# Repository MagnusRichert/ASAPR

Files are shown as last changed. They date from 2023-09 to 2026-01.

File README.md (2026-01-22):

# ASAPR - Advanced Scratch Assay Plotting Robot

This repository contains the code to execute in vitro cell analysis via scratch assays as done in the paper ["Scratching in style: 3D printers as plotters for automated and complex wound-healing assays"](https://doi.org/10.1016/j.isci.2025.114230). We greatly appreciate any feedback, contributions, or other input and questions you may have!

## How to use this repository

Here we will discuss how to use this repository for your scratch assay and what you need.

### Bill of Materials

- 3D-Printer that supports M0 command (preferrably with autoleveling sensor)
- Frame to hold your well plate
- 7mm wrench
- Adapter from M6 thread to tip
- Spring loaded pipette tip

These are the general materials you will need. The specific components used in the preprint are detailed in the BOM.xlsx file.

### Preparation of Printer

This chapter covers all the essential steps to prepare the printer. If you don't have access to a second printer for printing the frame, it's recommended to use the printer intended for scratching to print it. Be aware that whenever you home the printer, the tip should be removed to avoid it being driven into the build plate, which could cause damage!

#### Replace the nozzle

The first step is to remove the nozzle of the old printer with a 7mm wrench. Afterwards screw in the adapter with M6 thread that will be used to hold the tips. As described in the preprint there are two different approaches used to mount the probe to the printer. The first approach was to use a drill chuck holding the spring-loaded test probe while being inserted into a 3D-printed mount, considering that most of the 3D-printers have a M6 thread to hold the nozzle this method was not very straightforward. So the second approach was to 3D print a M6 Adapter as a direct replacement to the nozzle. 

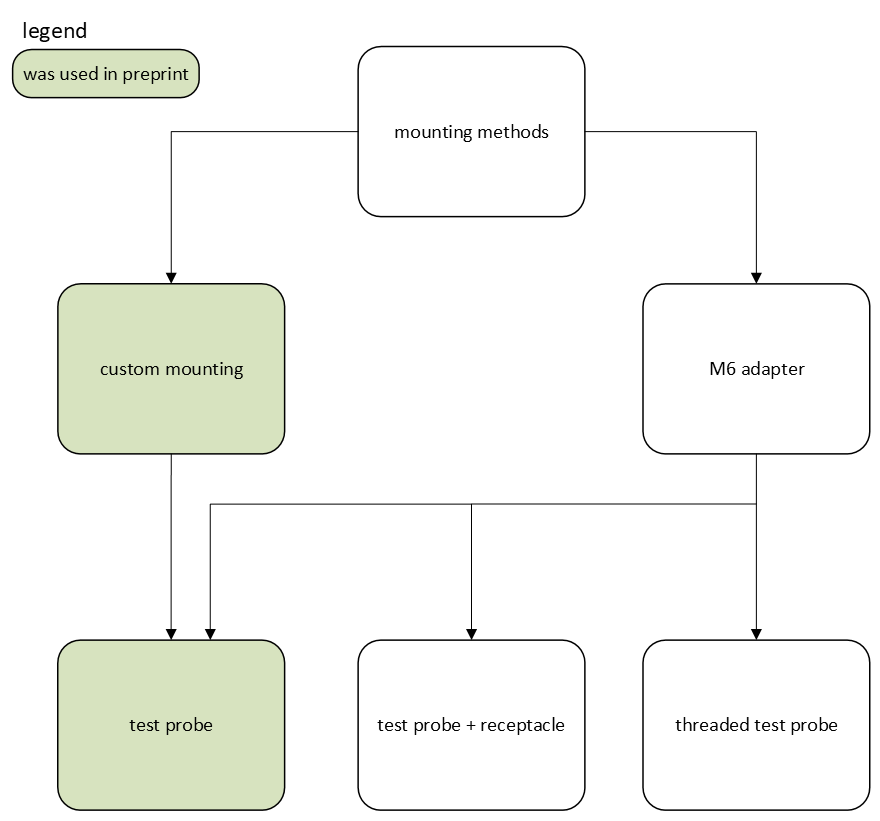
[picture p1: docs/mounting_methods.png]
mounting methods


As you can see there are multiple ways of mounting the test probe to the Printer, where three of these were used in the preprint. The other methods are still in work and not verified yet but may offer a few advantages.
When selecting the test probes for ASAPR there three main requirements to be fulfilled:

  1. The total length of the test probe must be greater than the depth of the well
     (in our case the length had to be at least 20mm excluding the part sitting in the Adapter)
  2. The width of the test probe must be wider than the inner diameter of the pipette tip
  3. The test probe should have a conical tip
     
You might also want to take a look at the force of the spring at the given compression point. We always looked for test probes with a spring force of 1.5N at the recommended working stroke provided in the datasheet. As the recommended working strokes are different for some test probes the spring force should be within the same order of magnitude. Furthermore you should take a look at the wobble of the test probe which describes the deflection of the tip from its ideal position due to the necessary play between the piston and the probe sleeve. To give you some idea of possible test probes, here are a few examples from the company INGUN Prüfmittelbau GmbH.

test probes:
- GKS-050 201 050 A 1500 
- GKS-912 201 060 R 1504 +KS-112 (currently supported)
- GKS-112 201 080 R 1504 +KS-112 (currently supported)
- GKS-112 201 100 A 1504 +KS-112 (currently supported)
- GKS-204 201 130 R 1510

threaded test probes:
- GKS-075 201 064 A 1502 M 
- GKS-112 201 080 R 1502 M (currently supported)
- GKS-112 201 100 R 1502 M (currently supported)
- GKS-204 201 130 R 1510 M
- GKS-503 201 180 R 1502 M (currently supported)

#### Level the printbed (Not needed with autoleveling)

To level the print bed, start by homing the printer, then disable the motors to allow free movement of the printhead in the XY-plane. Slide a sheet of paper between the adapter in the printhead and the print bed. Visit each corner and adjust the screws by tightening or loosening them until you feel slight resistance when moving the paper. Ensure the resistance is consistent across all corners. Alternatively, you can level the bed visually, making sure the distance between the adapter and the print bed is uniform at each corner. The exact distance isn't crucial, as the Z-offset will be set later.

#### Autolevel the printbed

If you want to use auto-leveling, you must first delete any old mesh, then create and save a new one for your print bed. The necessary actions can be found in the printer settings. For detailed guidance, there are many online tutorials available that explain this process step by step.

#### Mount the positioning for your wells

The next step is to mount your positioning guide for the well on the build plate. It's important to ensure the sides of the guide or well align with the X and Y axes. A magnetic print bed is not recommended, as it may slip and lose its position. If you're working with wells of different sizes, it's recommended to use permanent position guides in the lowest XY corner and variable guides for the other sides (see the picture below).

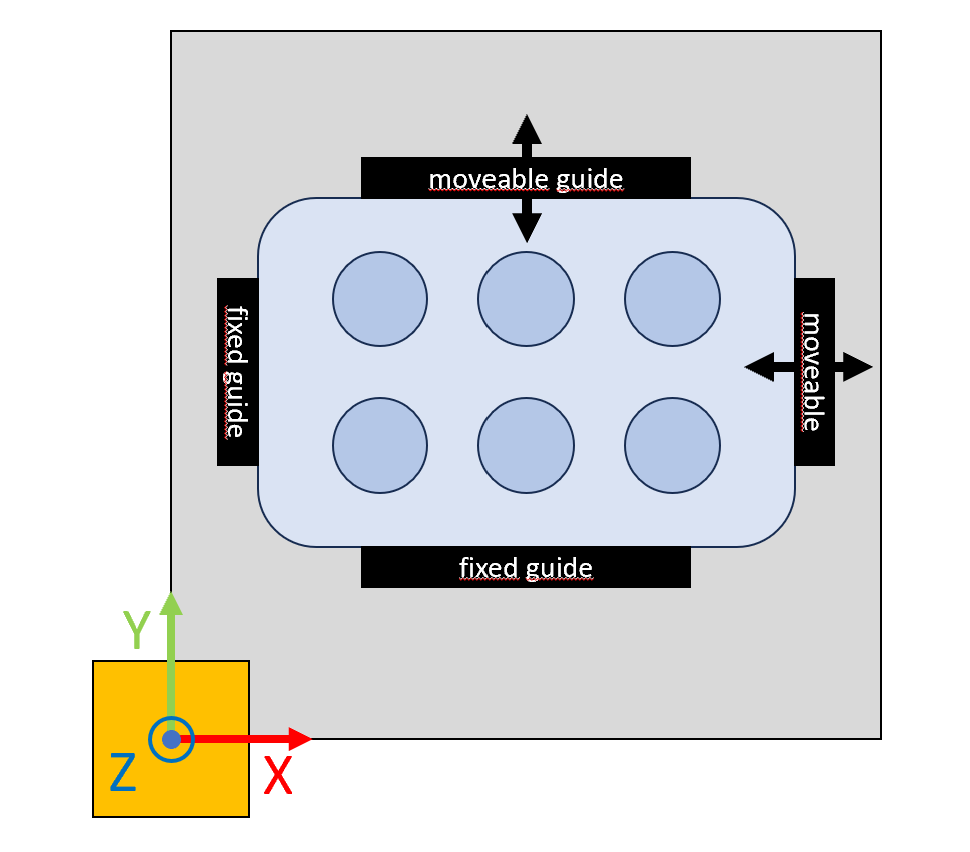
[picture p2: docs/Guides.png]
Guides


This setup allows you to determine the x_offset and y_offset only once. The offsets are shown in the picture below.

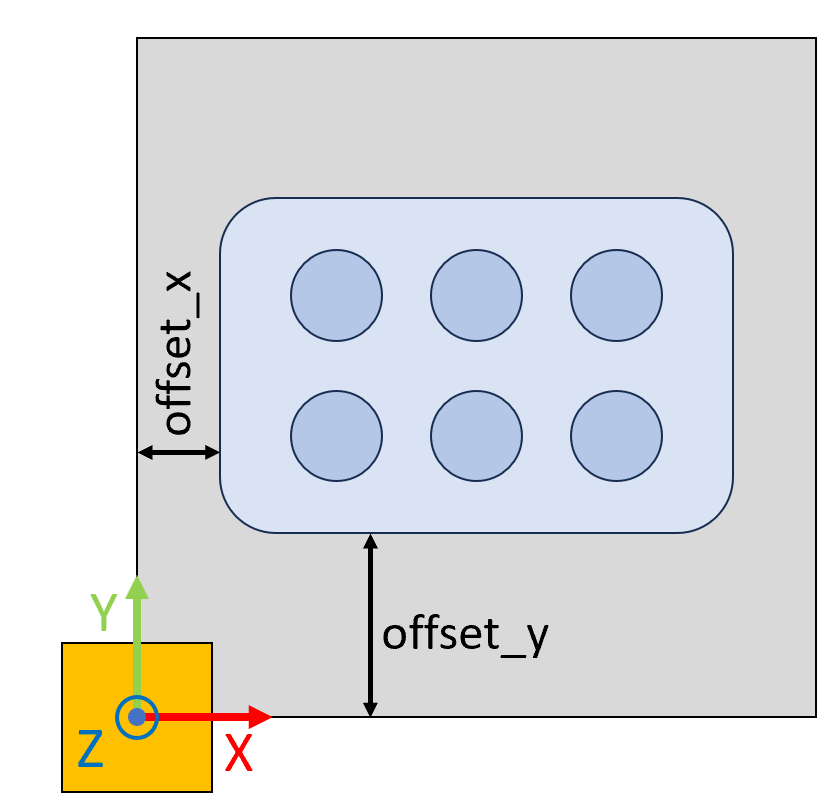
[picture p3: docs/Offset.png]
Offsets


The positioning guide used in the preprint can also be found in this repository. It can be printed using the same printer that will be used for scratching.

#### Measure offsets

There are two approaches to determining the offsets. The first method uses the printer's built-in "move" function and can be applied to any printer. The second method involves manually measuring the offset from the coordinate origin.

##### Using the printer

To measure the offsets, start by homing your printer and placing the well on the build plate. Use the printer's "move" function to raise the Z-axis high enough to insert a tip. As you move the axes, the printer will display the current position, which is the offset you need.

First, move the tip to the X and Y edges closest to the home position, ensuring it barely touches the edges. For instance, in the example image, the printhead was moved to 24.8mm for the Y-axis:
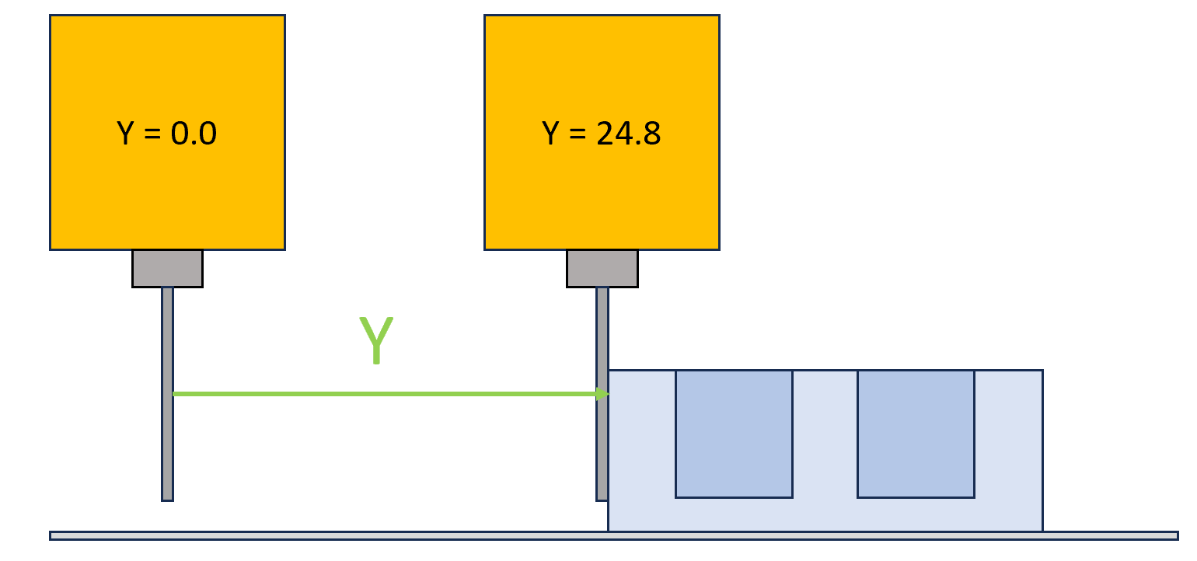
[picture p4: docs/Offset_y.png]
Offset Y

To calculate the offset for X and Y, add the radius of the tip used. For example, if the tip diameter is 0.4mm, the offset for Y would be: offset_y = Y + d/2 = 24.8mm + 0.2mm = 25.0mm

For the Z offset, move the printhead until the tip touches the well, as shown:
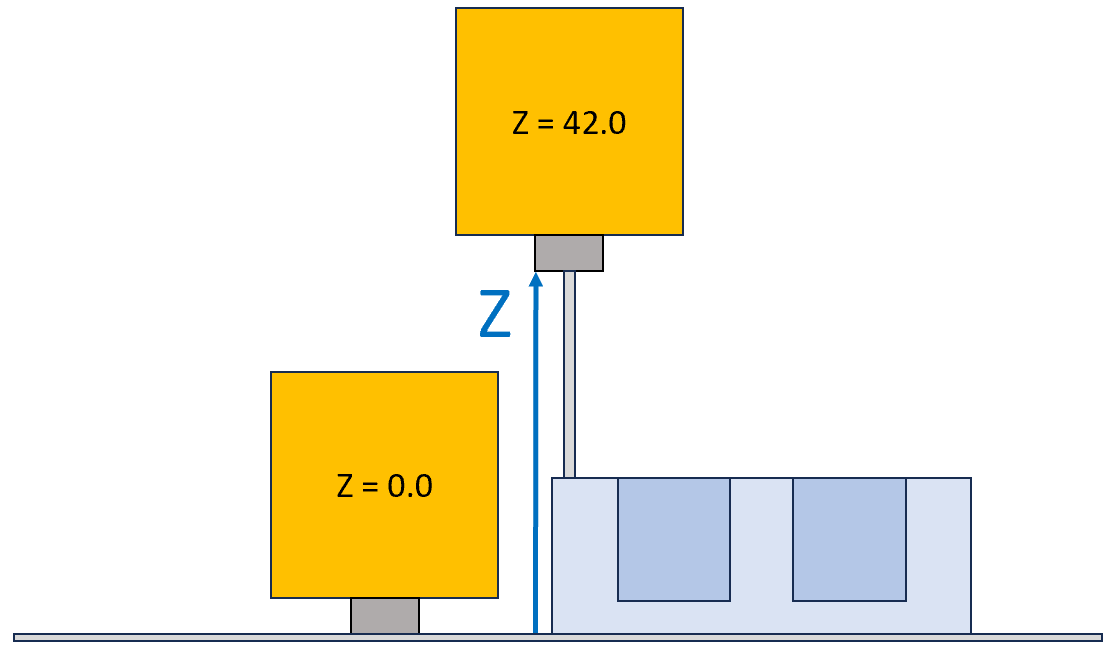
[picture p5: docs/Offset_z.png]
Offset Z

The Z value displayed can be used directly as the offset. If you change the tip, you'll need to adjust the Z offset by either remeasuring or calculating the difference in length between the tips and adjusting accordingly.

##### Calculating from coordinate system

This approach can be used if the printer's coordinate origin is marked on the build plate. You can simply measure the distance between the well plate and the origin in the X and Y dimensions using a caliper gauge. However, the Z offset still needs to be determined using the method described above, by moving the printer until the tip touches the well.

##### Fine tuning by test runs

The easiest way to set the X- and Y-axis offsets very accurately is to use an empty cell culture plate and scratch a cross through it using a test probe without a pipette tip attached so that the well surface is actually damaged. To do this, select the “mesh” option in the script with a 90° rotation and a generous tip offset to avoid hitting the edges of the plate in case of doubt. The test probe should not be driven too deeply into the plate in order to avoid tilting the tip and possible bending. You can then measure the localisation of the cross within the plate with a caliper and adjust the coordinates if necessary. Recommended is for example to measure all corners of a 24-well plate. Run again until it fits your needs.
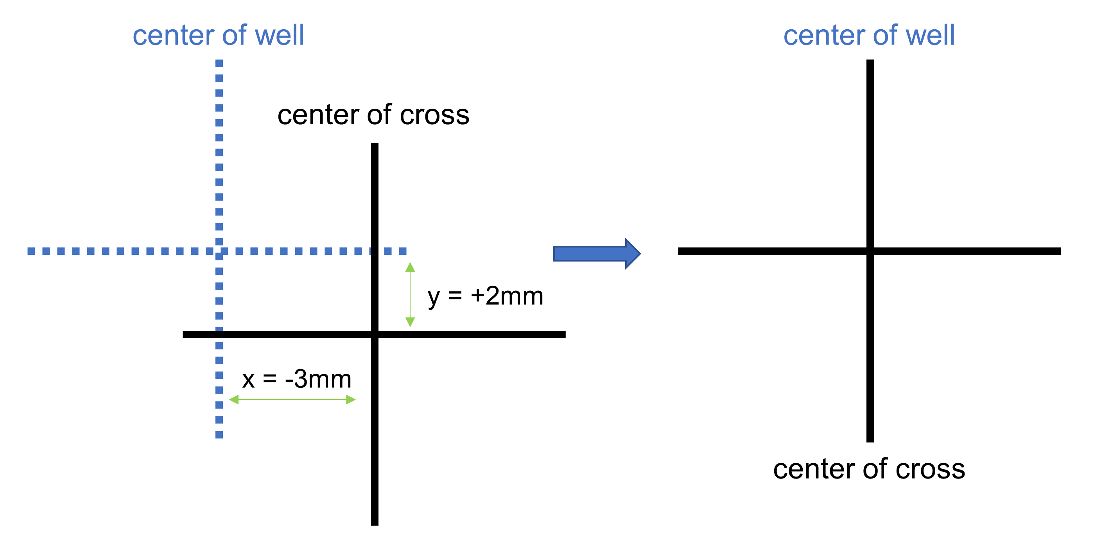
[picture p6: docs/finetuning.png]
Fine Tuning


#### Prepare well file

The program reads well dimensions from a file, which you will need to input manually based on your well. These specifications can typically be found in the product's technical documentation or you can measure them yourself. An example file for a four by six well plate is provided in the repository. It contains the following dimensions:

~~~bash
number_x: 3
number_y: 2
diameter: 15.5
depth: 17.3
distance_well: 3.5
distance_x: 7.8
distance_y: 6.0
~~~

The values for number_x and number_y represent the number of wells along the x and y axes, respectively. Be aware that they depent on the orientation of your well. The remaining dimensions are displayed in the image below.
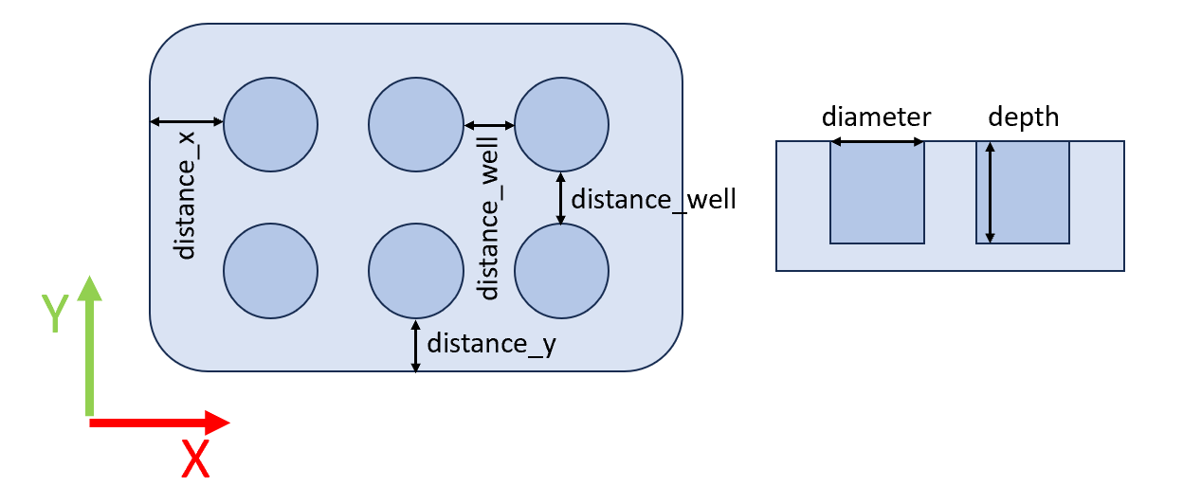
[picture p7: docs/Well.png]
Well Dimensions


### Preparation of your PC

You will need an installation of python version 3 or newer. When installing check the box that says "Add Python to PATH". Afterwards open a command window like powershell or cmd and enter the following commands sequentially:

~~~bash
python -m ensurepip --upgrade
pip install svgpathtools
~~~

This will install the python package manager and the package svgpathtools which is needed to process vector graphics.

### Script usage

After measuring all the required offsets and preparing your PC, you’re ready to use the script. If Python is installed correctly, you can simply double-click ASAPR.py to run it.

The GUI will appear as shown below:
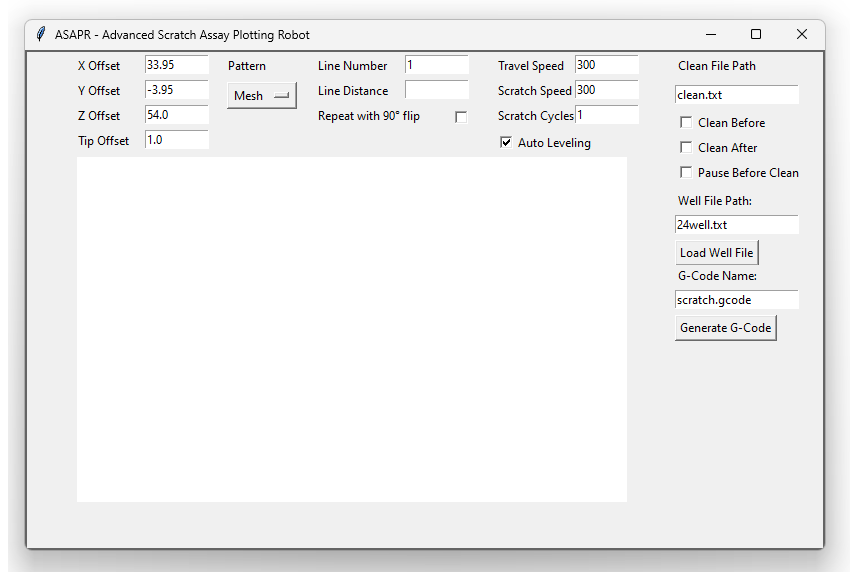
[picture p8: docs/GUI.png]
GUI


#### Enter offsets

In the top left of the GUI, you need to enter your measured offsets in millimeters. The tip offset specifies the minimum distance between the center of the tip and the well wall. This value MUST be at least half of the tip diameter. For more robust scratching, you might consider increasing this offset to 1-2 mm.

#### Choose pattern

Next to the offsets you can choose between between three different patterns: mesh (mutiple lines), circles and svg grapics.

##### Mesh

The mesh pattern is defined by the number of lines and the distance between them. You can also just choose to scratch a single line through the center of the well. If the "Repeat with 90° flip" box is checked, the mesh will be scratched again rotated by 90° to create a criss-cross pattern.

Mesh

##### Circles

The circles pattern is defined by the number of circles, the distance between them, and the diameter of the innermost circle.

Circles

##### SVG

To scratch a vector graphic, place the file in the same folder as ASAPR.py and enter its name. The SVG should contain only lines and curves, which can be filled. For this you can specify the overlapping area between the fill lines from 0 to 1 (0 to 100%). Currently only the fill property of the style attribute is supported, so not all SVG Files will work. Best practice is to generate a new basic SVG File with inkscape and not to use complex forms or properties. The scratch will follow the lines like a trajectory, so you can create larger surfaces by placing lines close to each other. The SVG will be scaled automatically to the maximum size that fits within the well. If you want it to be smaller, you can adjust the scale parameter to values between 1 (maximum size) and 0 (essentially a point).

SVG

#### Movement settings

Next to the patterns, you can set the movement speed of the printhead during both movement and scratching, in mm/s. Note that there are limitations to these speeds in the printer settings, especially for the Z-axis speed. If you want to scratch your pattern multiple times, you can increase the "Scratch Cycles" value from 1 to however many cycles you desire. To enable the auto-leveling function of your printer, check the corresponding tickbox.

#### Cleaning

To clean the tip before or after scratching a well plate, you can set up one or more cleaning containers and specify their coordinates in a "clean.txt" file. The cleaning process involves moving the tip in a specified number of circles within each container. Below is an example of the file content format:

~~~bash
X: 150
Y: 120
Z: 30
Radius: 4
Depth: 10
Number: 20
/
~~~

In this file, each section describes a cleaning container, with Number specifying the amount of circles, Depth indicating how deep the circles will be relative to the specified Z coordinate, and Radius defining the size of the circles. The "/" marks the end of the data for one container, and you can add as many sections as needed in one file.

When the "Pause Before Clean" checkbox is ticked, the tip will pause 1 cm above the specified XYZ coordinates. This allows you to position your cleaning container more easily without needing to measure the coordinates precisely.

##### Desinfecting
To disinfect the tip, it is sufficient to immerse it in 70% ethanol for at least 30 seconds and then allow it to air dry. It is also recommended to rinse the tip in ethanol after each scratching process to remove debris. During the test phase, several scratched wells plates were incubated for at least one week and contamination was never observed. It is also possible to prepare several tips and autoclave them in advance, but it is not necessary to replace them after each use.

#### Load well setting

On the right side of the GUI, you'll need to provide the well data. Since wells are often standardized, the data is read from a *.txt file for ease of sharing, modification, and reuse. An example file named "24well.txt" is included in the repository.

#### Select wells to scratch

After loading the well file, the layout will be plotted in the central area of the GUI. Clicking on a well will turn it red, indicating that it will be excluded from scratching. You can also click and drag your mouse to select or deselect multiple wells underneath. The well located in the bottom left corner represents the one closest to the coordinate origin, which is typically the home position of your printer and usually corresponds to the bottom left corner of the print bed.

#### Generate G-Code

The final step is to enter the name of your *.gcode file and to generate the G-Code. BEFORE running it on the 3D-Printer be sure to read the next chapter for important instructions. In the future there might be the option to send the generated G-Code right from the GUI over W-Lan, until then you need to save the G-Code on a SD-Card and plug into the 3d-printer.

##### Individual customisation of the G-Code

Some printers may require individual adjustments, especially in the header section of the Gcode. For example, the Prusa MK3S+ requires an additional 'W' after the G28 command to suppress auto levelling, which is not possible in the setup due to the fixed plate holder. These adjustments can easily be made in the text file of the finished Gcode. An option to customise the header of the Gcode for each printer individually is planned.

~~~bash
G28 W
~~~

### Running the G-Code

Before running the G-Code on your machine, ensure that the bed is leveled or properly prepared for the auto-leveling option. The guides and well should be correctly positioned by now. Additionally, remove the scratching tip, as the printer will home before starting the scratching process; leaving the tip in place could cause it to be driven into the print bed. If the printer does not home the Z axis above the print bed, but at the end stops of the upper area, the tip can always be left in place.

Once you start the print, the "M0" G-Code command will pause the printer before scratching, allowing you to insert the tip. Verify that your printer firmware supports this command. After inserting the tip, continue the print, usually by pressing the knob.

You can preview how your scratches will look by pasting your G-Code into a viewer. One option is ncviewer.com, though keep in mind that for larger X and Y coordinates, the depiction might be shifted. Despite this, the G-Code will still function correctly on your printer.

## Outlook

A lot of ideas went into this project and even more were discarded. There is certainly room for improvement in every nook and cranny, so we would be delighted to receive any valuable input for the further perfection of this project. Be it software improvements or better materials such as a Teflon tip, etc. Your input is always highly appreciated!

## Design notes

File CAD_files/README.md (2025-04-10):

# CAD files

In this section we want to go into detail on how to print and assemble the needed parts mentioned in the BOM file.

## frame

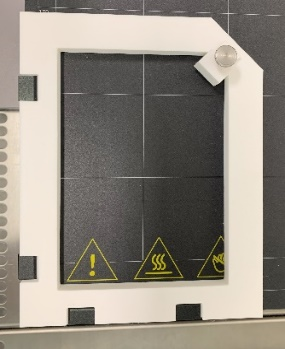
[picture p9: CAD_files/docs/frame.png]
frame


The frame is supposed to hold the well plate on the print bed while maintaining a fixed position consistently. The frame itself is attached with four clamps designed for glass print beds. For the frame you need in total four pieces, of which are two 3D-printed. Both of these parts are included in the file "frame".
In general there are two things which have to be considered when printing the frame. Since the frame features some floating areas you want to enable some kind of support, preferably tree support for printing. Moreover it is preferred to add some kind of modifier in the area of the slider to increase the infill density since this section of the frame is under more mechanical stress.

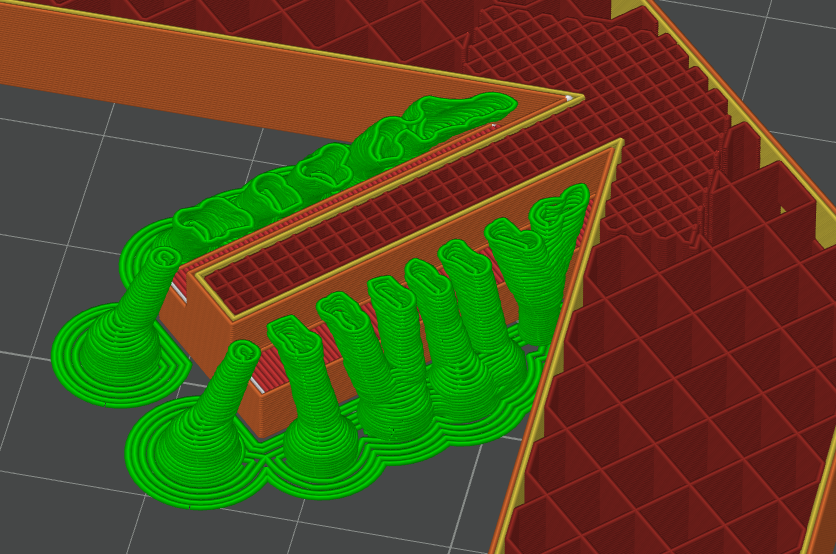
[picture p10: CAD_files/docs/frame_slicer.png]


As you can see tree support was used while achieving a higher infill density in the slider area. The frame itself was printed with an infill density of 15% while the area of the slider has an infill density of 70%. Every part was printed with a 0.4mm nozzle and a layer height of 0.2mm using white PLA on the BambuLab A1 mini.

Since the screw for securing the slider on the frame has to be screwed in and out a few times we decided to use an M3 threaded insert for the slider. This ensures a tight fit of the screw even after several iterations of use. Last but not least you need an M3 knurled knob for the slider.
These two parts are more or less optional since you could also think of just using a normal M3 screw without threaded insert.

print settings:
- infill density: 15%-70%
- nozzle diameter: 0.4mm
- layer height: 0.2mm
- material: PLA

## M6 adapter

The M6 adapter is needed to mount the spring loaded test probe to the printhead of the printer. As mentioned in the preprint this option is preferred over using the mounting block together with the drill chuck. The adapters are quite similar, but in this section, we will go into detail on how to print them. The following test probes are currently supported:

| test probe (just an example)  | print file | suitable pipette |
| ------------- |:-------------:| -----:|
| GKS-912 201 060 R 1504 | adapter_M6_2_15mm.step | 10μL  |
| GKS-112 201 080 R 1504 | adapter_M6_2_15mm.step | 200μL |
| GKS-112 201 100 A 1504 | adapter_M6_2_15mm.step | 200μL |
| GKS-112 201 080 R 1502 M | adapter_M6_M1_6.step | 200μL |
| GKS-112 201 100 R 1502 M | adapter_M6_M1_6.step | 200μL |
| GKS-503 201 180 R 1502 M | adapter_M6_M2_5.step | 1000μL |

### M6 adapter without thread

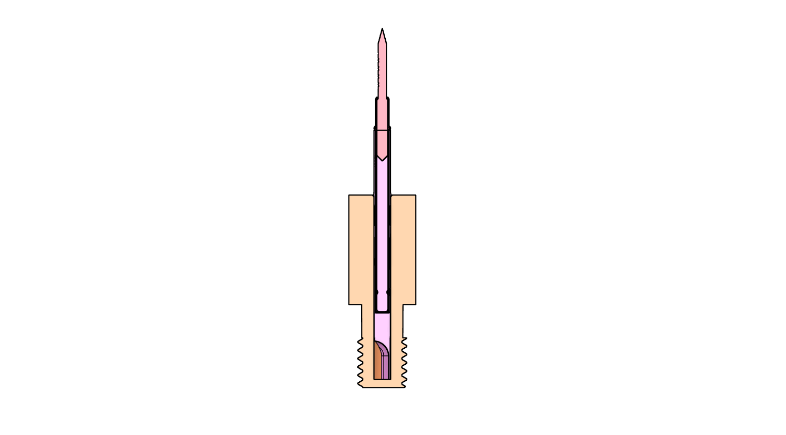
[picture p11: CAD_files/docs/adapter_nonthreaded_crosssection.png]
adapter_nonthreaded_crosssection


This adapter is used with the non threaded test probes and is designed to be used with a receptacle. It could also be used without receptacle but you might have to play around a little bit with X-Y hole compensation in the slicer settings to get a good press fit.
To increase first layer adhesion the M6 thread points upwards while printing. Once again you may have to adjust the hole compensation in the slicer to get a good fit of the receptacle. Note that the width of the M6 thread can also be adjusted in the slicer if the fit is too loose or too stiff. More information on this topic can be found [here](https://wiki.bambulab.com/en/software/bambu-studio/xy-hole-contour-compensation). Since the most complex shape in this print is the M6 thread you might also want to decrease the layer height for this section. While prototyping we used an adaptive layer height profile to avoid a further increase in total printing time. You can find more on the topic [here](https://wiki.bambulab.com/en/software/bambu-studio/adaptive-layer-height).

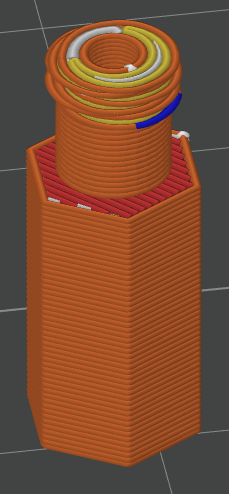
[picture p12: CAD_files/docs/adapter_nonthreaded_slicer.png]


print settings:
- infill density: 40%
- nozzle diameter: 0.2mm
- layer height: 0.04mm
- material: PLA

### M6 adapter with thread

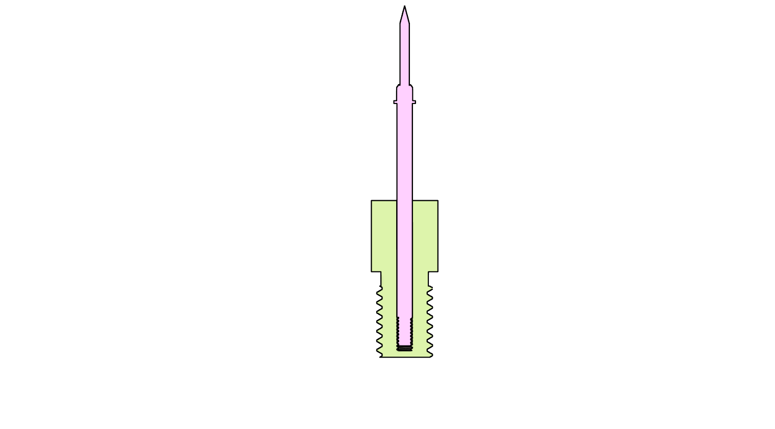
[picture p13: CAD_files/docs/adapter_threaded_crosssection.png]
adapter_threaded_crosssection


This adapter is used with the threaded test probes, mostly recognizable by the M in the name. In general the topics mentioned above have to be considered with this adapter too since they are very simillar. In our case the printed thread was a little bit too small, so we had to adjust the X-Y hole compensation which solved this issue.  One major difference is the nozzle used. Since the thread of the test probe is very small (in our case M1.6 and M2.5) we used a 0.2mm nozzle with a layer height of 0.04mm in the section of the thread. The initial layer height was 0.08mm to avoid first layer issues. 

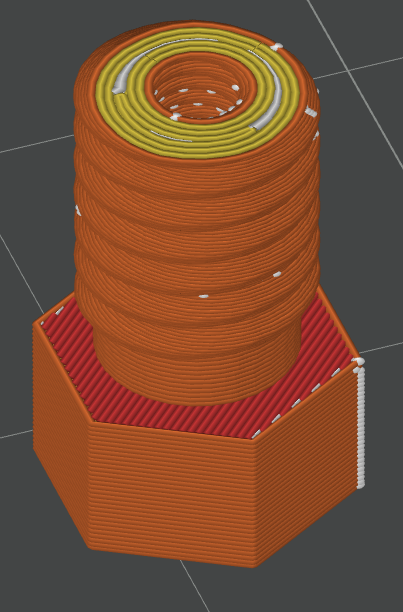
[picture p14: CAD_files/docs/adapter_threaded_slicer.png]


print settings:
- infill density: 40%
- nozzle diameter: 0.2mm
- layer height: 0.04mm
- material: PLA

## cutting device

The cutting device is used to trim pipettes to a suitable length and consists of six parts, three of which are 3D-printed. A standard cutter knife blade—commonly available at most hardware stores—is used for the actual cutting process. An M5 screw and nut are used to hold the assembly together. (See pictures below.)
An adaptive layer height profile was used once again to achieve greater detail in the areas of the moulds that hold the pipettes. For the part of the print that snaps onto the other component, support structures were used during printing.

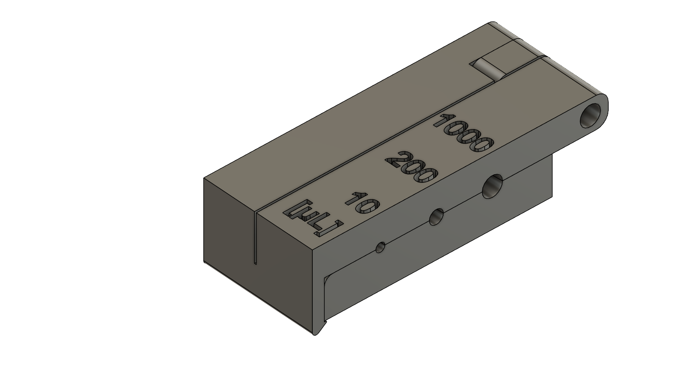
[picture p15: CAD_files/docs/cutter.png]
cutter


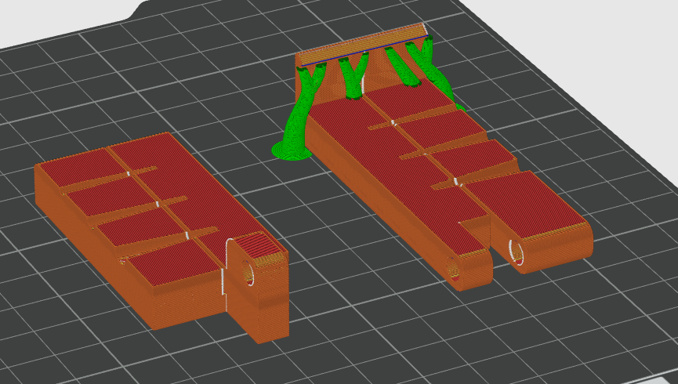
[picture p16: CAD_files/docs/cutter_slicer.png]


print settings:
- infill density: 20%
- nozzle diameter: 0.2mm
- layer height: 0.2mm
- material: PLA

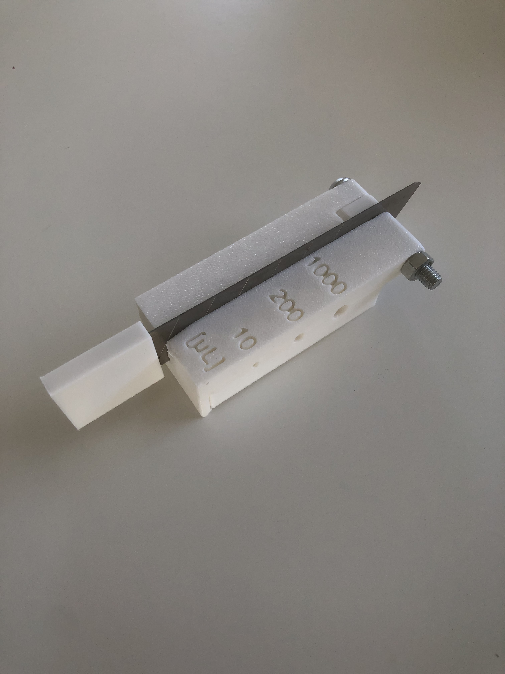
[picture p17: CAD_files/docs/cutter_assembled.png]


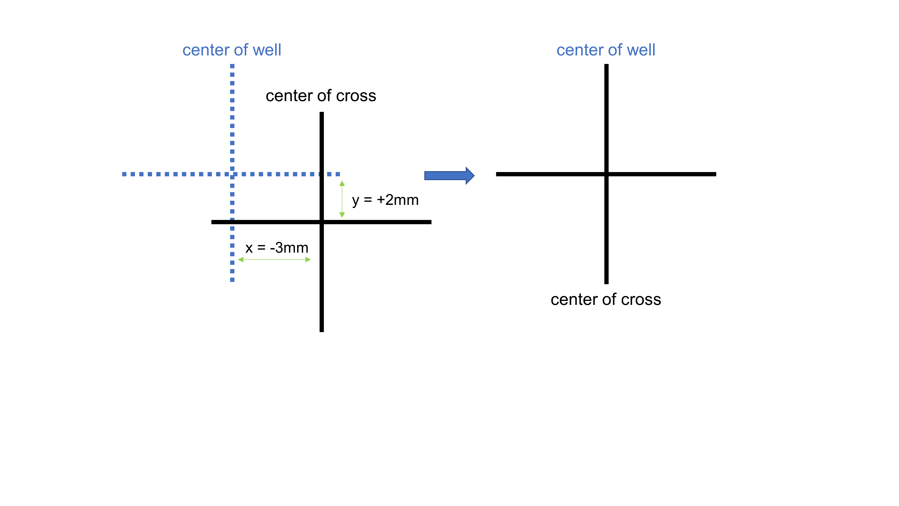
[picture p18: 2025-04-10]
docs/fine tuning.png

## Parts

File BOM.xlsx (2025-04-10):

 | Item # | Component | Description | Quantity | Package Quantity | Unit Cost | Total Cost | Mfg | Sourcing Link
Hardware
3D-printed parts
 | 1 | frame + slider | 3D-printed part to fix the well on the print bed, ensuring the same postion time after time | 1 | 1 | ~ 1,30€ | ~ 1,30€ | self-made | GitHub(CAD files)
 | 2 | M6 adapter | adapter for mounting the spring loaded (either with thread or without) test probe to the printhead | 1 | 1 |  |  | self-made | GitHub(CAD files)
 | 3 | cutter | device for cutting pipettes to the same length repeatable | 1 | 1 |  |  | self-made | GitHub(CAD files)
parts to purchase
 | 4 | 3D-printer | a FDM 3D-printer e.g. Snapmaker A350® or Prusa MK3S+® | 1 | 1 | depends | depends | depends
 | 5 | threaded insert | M3 threaded insert (short) for the slider of the frame | 1 | 100 | 0.089 € | 8.90 € | CNC KITCHEN | M3 threaded insert (https://www.amazon.de/CNC-KITCHEN-Original-Gewindeeinsatz-Version/dp/B09FXNX6WF?__mk_de_DE=%C3%85M%C3%85%C5%BD%C3%95%C3%91&language=de_DE)
 | 6 | knurled knob | screw for the slider of the frame (goes into threaded insert) | 1 | 1 | 0.95 € | 0.95 € | Ganter | knurled knob (https://www.normteile-leinigen.de/Raendelschraube-M3-x-6-hoch-DIN-464/464-M3-6-ZB)
 | 7 | clamps | clamps to fix the frame (item 1) on the print bed | 4 | 10 | 0.80 € | 7.99 € | FASBET | clamps (https://www.amazon.de/Hei%C3%9Fbett-Glasplattform-3D-Drucker-Hei%C3%9Fbett-Glasplatte-Einstellbare-Halterung/dp/B0BVMGVBYK)
 | 8 | test probe | spring loaded test probe for holding the pipette (more information see README | 1 | 1 | depends | depends | INGUN Prüfmittelbau GmbH | Ingun (https://ingun.com/)
Software | 9 | ASAPR.py | GUI for generating G-Code for the 3D-printer (for detailed description see GitHub) | 1 | 1 | 0 | 0 |  | GitHub

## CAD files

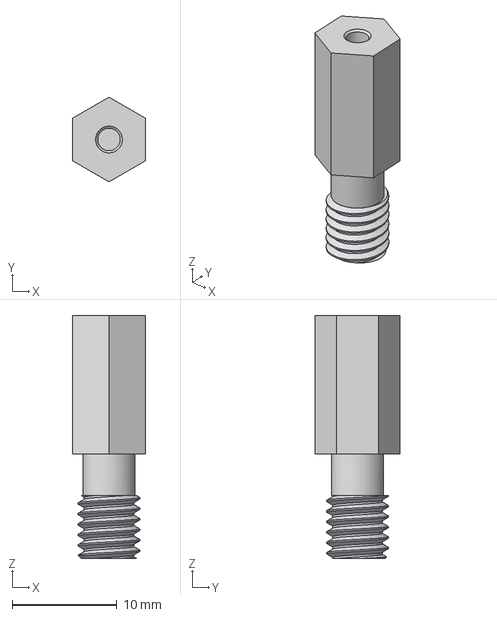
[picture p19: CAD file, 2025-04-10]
CAD_files/adapter/for_non_threaded_test_probes/adapter_M6_2_15mm.step
7.00 x 8.08 x 23.2 mm

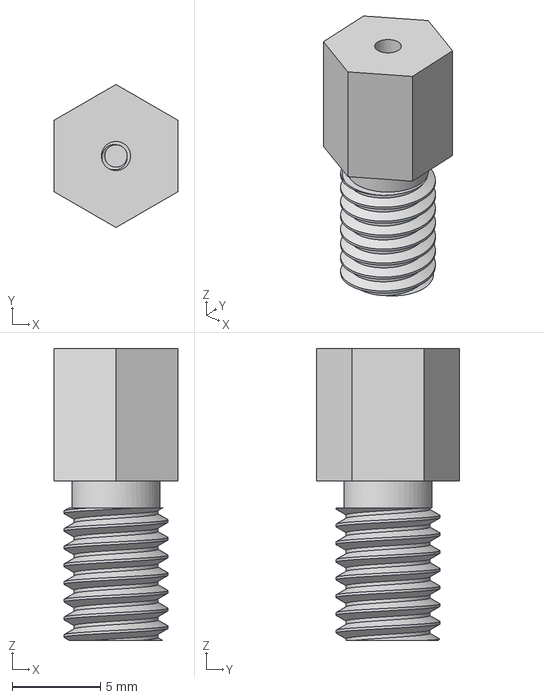
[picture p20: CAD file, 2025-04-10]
CAD_files/adapter/for_threaded_test_probes/adapter_M6_M1_6.step
7.00 x 8.08 x 16.5 mm

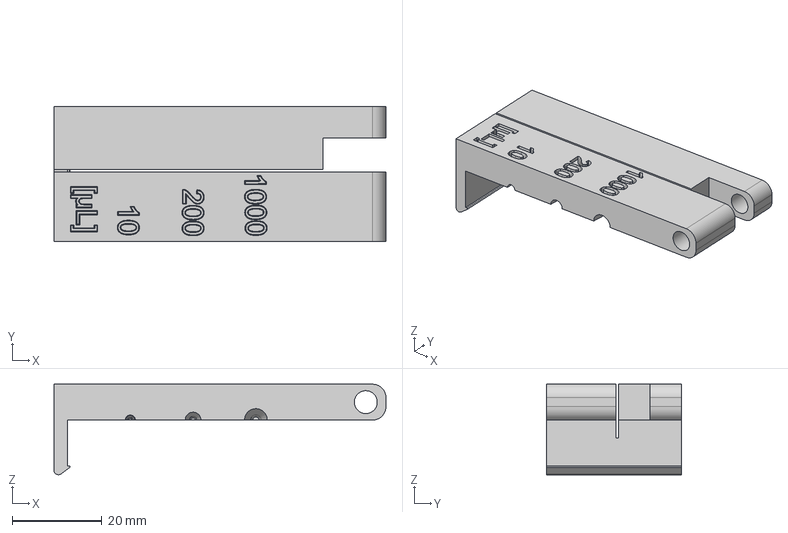
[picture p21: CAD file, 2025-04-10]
CAD_files/cutter/cutter_part2.step
74.0 x 30.0 x 20.2 mm

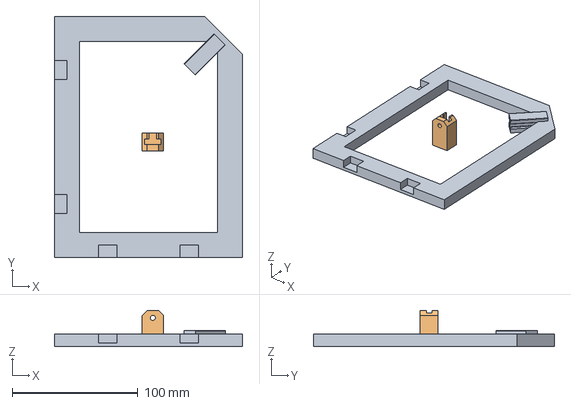
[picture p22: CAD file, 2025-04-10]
CAD_files/frame/frame+slider.step
150.0 x 192.0 x 29.0 mm
Komponente1
schieber_laenger

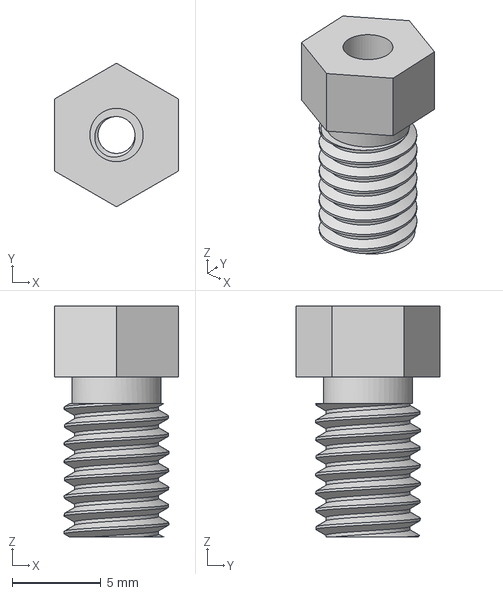
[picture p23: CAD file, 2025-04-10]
CAD_files/adapter/for_threaded_test_probes/adapter_M6_M2_5.step
7.00 x 8.08 x 13.0 mm

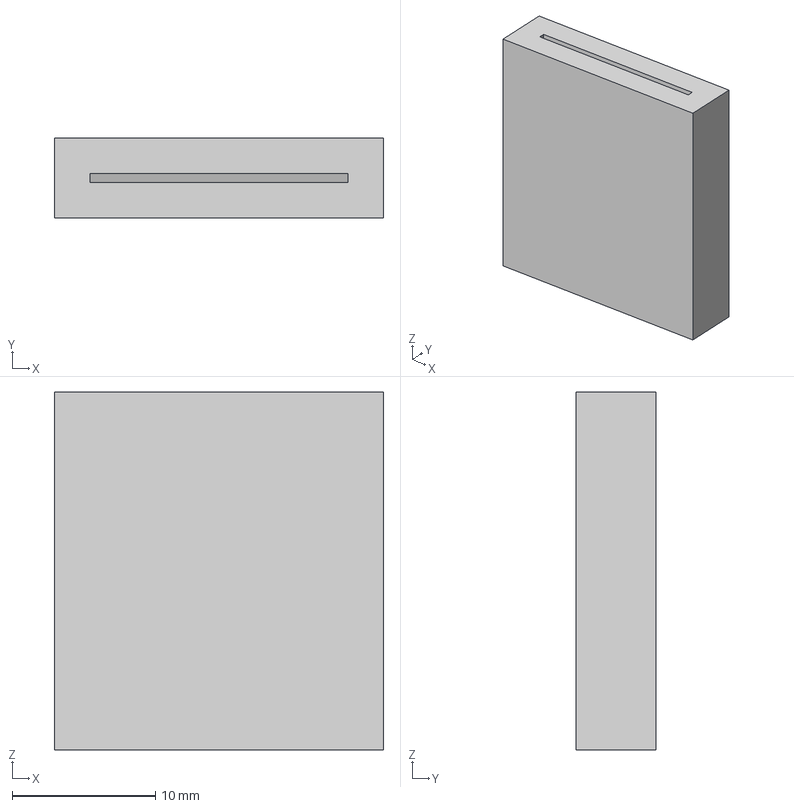
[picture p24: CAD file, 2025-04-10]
CAD_files/cutter/protection.step
23.0 x 5.60 x 25.0 mm

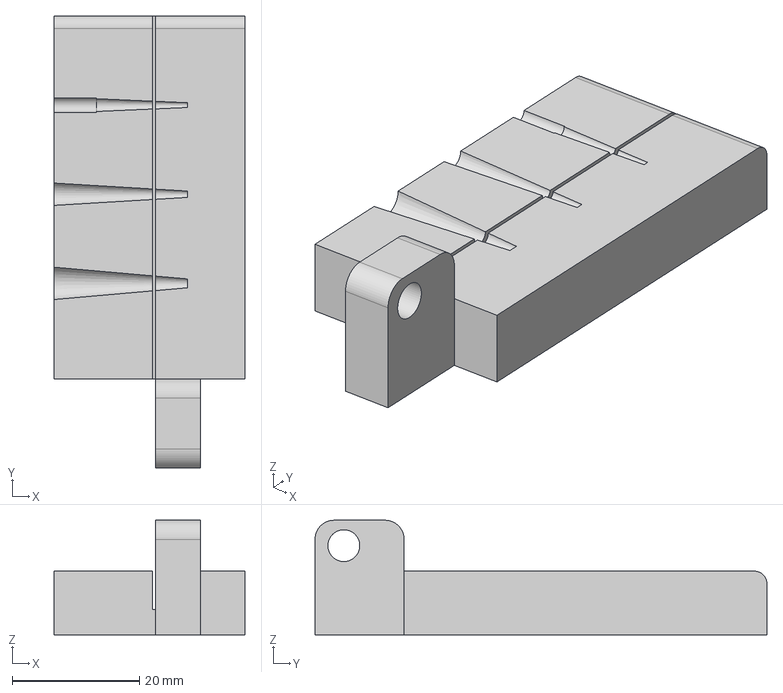
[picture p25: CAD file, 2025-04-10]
CAD_files/cutter/cutter_part1.step
30.0 x 71.0 x 18.0 mm

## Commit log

2024-09-15 Added BOM to Main
    Added Bill of Materials for performing Scratch Assay as mentioned in preprint
    [BOM.xlsx]
2025-02-23 Delete docs/mounting_methods.png
    revised picture
2025-03-02 continued work on README, added BOM and pictures.
    [BOM.xlsx, frame+slider.step]
2025-03-03 modified README, added adapter files
    [adapter_M6_2_15mm.step, adapter_M6_M1_6.step, adapter_M6_M2_5.step]
2025-04-10 added CAD files for cutter and worked on README
    [cutter_part1.step, cutter_part2.step, protection.step]
